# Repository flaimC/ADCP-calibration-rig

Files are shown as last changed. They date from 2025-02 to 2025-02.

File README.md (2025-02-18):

# ADCP-calibration-rig
This repo documents the design and build of an ADCP calibration rig for a Nortek Signature 100. The rig utilizes syntactic foam and a large footprint to stay afloat and stable in a calibration tank. It is designed to be lifted with an over-head crane while the ADCP is attached. Future versions of this calibration tool will include lasers, cameras, and motorized ball movement to expidite the calibration process.
adcpCalibrationRigAssy (3)

# Onshape CAD
This project was designed in a browser-based CAD program called Onshape. The document for this project can be found [here](https://cad.onshape.com/documents/10602cede9c07e59b6c9bb3e/w/70dcfadde18bdff9054825df/e/5ac3f072fa41a360b08c238f)

# ADCP calibration rig buoyancy calculation
### using Archimedes principle 
Archimedes principle states that the buoyancy of an object is equal to the mass of the water it displaces.

The buoyancy force of a fully submerged object is described as $F_B = V_{disp} \times \rho \times g$, where $V_{disp}$ is the displaced volume, $\rho$ is the density of the dsiplaced fluid, and $g$ is the gravitational constant.

We can expand on this equation to include the force of gravity acting upon the submerged object.

$$F_B = V_{disp} \times (\rho_{disp} - \rho_{object}) \times g$$

We can expand this equation and cancel out the gravitational constants to find the maximum mass a submerged volume of known density can support before being fully submerged.
$$M_{max} = V_{disp} \times (\rho_{disp} - \rho_{object})$$
For complex objects and geometries, the forces acting upon subcompenents need to be accounted.

$$M_{max} \times g = \left( \sum_{i=0}^n M_{i} \times g \right)$$
#### Define variables
Let,
$$B = \text{resultant maxium mass from chosen materials and volumes that can be supported without sinking},$$

$$\rho_{sw} = \text{assumed density of seawater in tech tank},$$
$$\rho_{syn} = \text{density of macrofoam-18 syntactic foam},$$
$$\rho_{hdpe} = \text{density of HDPE platstic sheet},$$
$$\rho_{misc} = \text{average density of submerged metal parts},$$

$$V_{syn} = \text{volume of syntactic foam},$$
$$V_{HDPE} = \text{volume of the HDPE sheet},$$
$$V_{misc} = \text{volume of submerged metal parts},$$

$$M_{ADCP} = \text{weight of ADCP in water},$$
$$M_{topmisc} = \text{weight of in-air metal parts}.$$
Note: The distrubtion of density variation does not matter for $\rho_{misc}$ since we are just looking for a buoyancy force, not stability. This density is calcuated from the total mass and volume of submerged metal parts (e.g., screws, nuts, rods).

#### Find the buoyancy
A buoyancy force is only calculated for submerged objects. The full mass of in-air objects is subtracted from the total bouancy. The top of the ADCP is not submerged, but the weight is nearly wholely contained at the bottom of the ADCP, so we are assuming the in-air weight of the top two-inches of the ADCP is negligible. Surface tension is also assumed to be negligible in this calculation.

$$B = V_{syn}(\rho_{sw}-\rho_{syn}) + V_{hdpe}(\rho_{sw}-\rho_{hdpe}) + V_{misc}(\rho_{sw}-\rho_{misc}) - M_{adcp} - M_{topmisc}$$

If $B > 0$, then the ADCP calibration rig should float. If $B < 0$, then the ADCP calibration rig should sink.

Given,

$$\rho_{sw} = 1035\text{ kg•m}^{-3},$$
$$\rho_{syn} = 290\text{ kg•m}^{-3},$$
$$\rho_{hdpe} = 941\text{ kg•m}^{-3},$$
$$\rho_{misc} = 3910.26\text{ kg•m}^{-3},$$

$$V_{syn} = 0.05968\text{ m}^3,$$
$$V_{HDPE} = 0.00509\text{ m}^3,$$
$$V_{misc} = 0.001306\text{ m}^3,$$

$$M_{ADCP} = 13\text{ kg},$$
$$M_{topmisc} = 4.8144\text{ kg}.$$

We can plug these values into our buoyancy equation and find the maximum in-air weight the calibration rig can hold before being completely submerged.

$$B = 0.05968 \text{ m}^3(1035 \text{ kg•m}^{-3}-290\text{ kg•m}^{-3}) +$$ 
$$0.00509\text{ m}^3(1035\text{ kg•m}^{-3}-941\text{ kg•m}^{-3}) +$$ 
$$0.001306\text{ m}^3(1035\text{ kg•m}^{-3}-3910.26\text{ kg•m}^{-3}) - 13\text{ kg}- 4.8144\text{ kg}$$

$$B=23.37 \text{ kg}$$

# Disclaimer
This repository is a scientific product and is not official communication of the National Oceanic and Atmospheric Administration, or the United States Department of Commerce. All NOAA GitHub project code is provided on an ‘as is’ basis and the user assumes responsibility for its use. Any claims against the Department of Commerce or Department of Commerce bureaus stemming from the use of this GitHub project will be governed by all applicable Federal law. Any reference to specific commercial products, processes, or services by service mark, trademark, manufacturer, or otherwise, does not constitute or imply their endorsement, recommendation or favoring by the Department of Commerce. The Department of Commerce seal and logo, or the seal and logo of a DOC bureau, shall not be used in any manner to imply endorsement of any commercial product or activity by DOC or the United States Government.

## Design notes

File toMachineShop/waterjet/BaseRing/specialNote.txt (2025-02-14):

Note: It is intended for the counter bore hole to be done after the main hole is water jet cut.

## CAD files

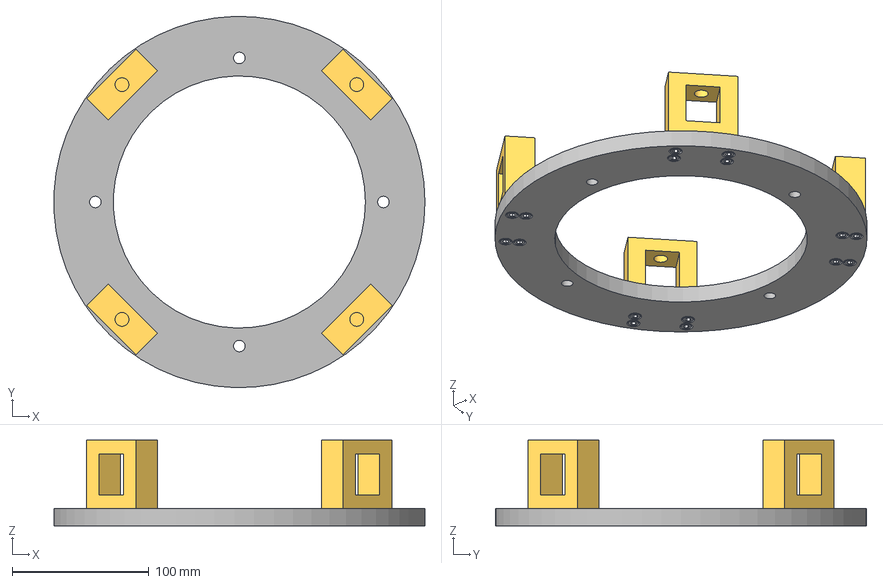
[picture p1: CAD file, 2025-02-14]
stlFiles/mountAssy.step
270.8 x 270.9 x 62.7 mm
AdcpMountBlock x 4
AdcpMountBasePlate
10-32 1in x 16

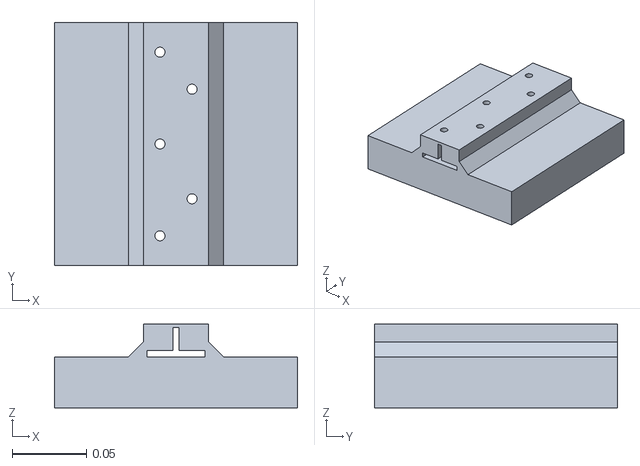
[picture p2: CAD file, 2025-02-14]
stlFiles/3dPrintable/ballast - outriggerMount.stl
0.164 x 0.164 x 0.0566

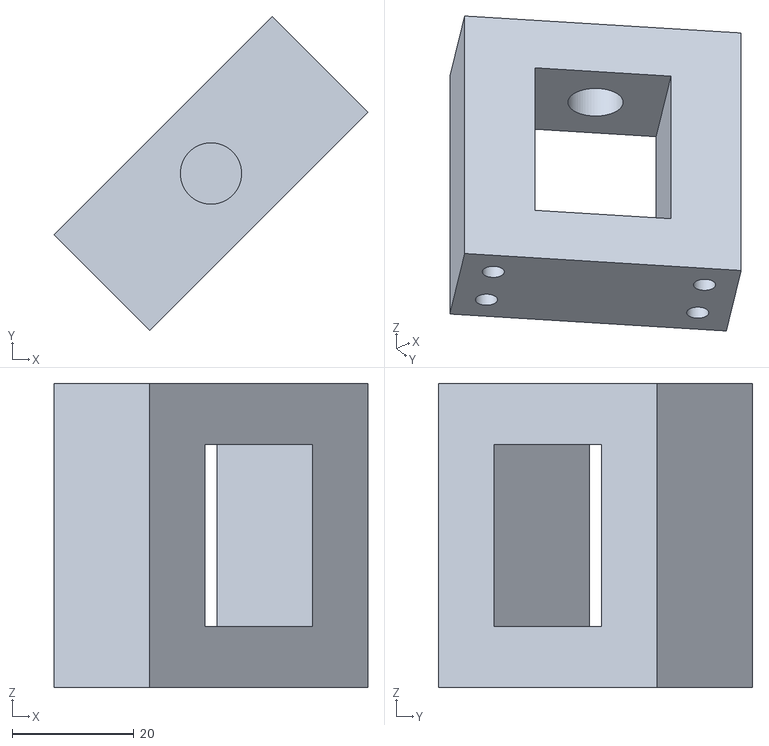
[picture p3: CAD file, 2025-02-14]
toMachineShop/machined/mountBlock/mountBlock.stl
51.6 x 51.6 x 50.0

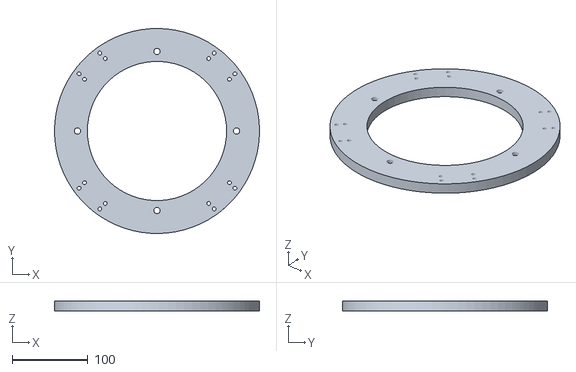
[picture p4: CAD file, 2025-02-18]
toMachineShop/waterjet/adcpMountBasePlate/AdcpMountBasePlate.stl
271.0 x 270.9 x 12.7

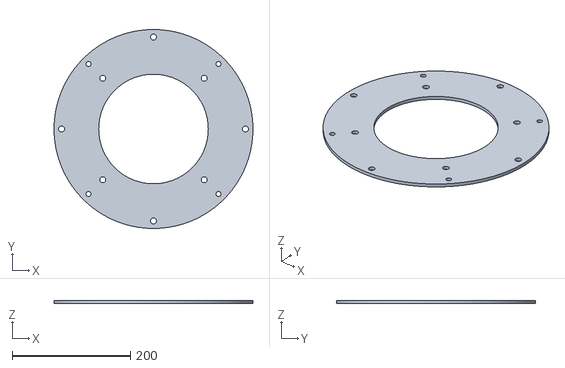
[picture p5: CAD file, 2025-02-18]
toMachineShop/waterjet/BaseRing/baseRing.stl
336.0 x 336.0 x 5.00

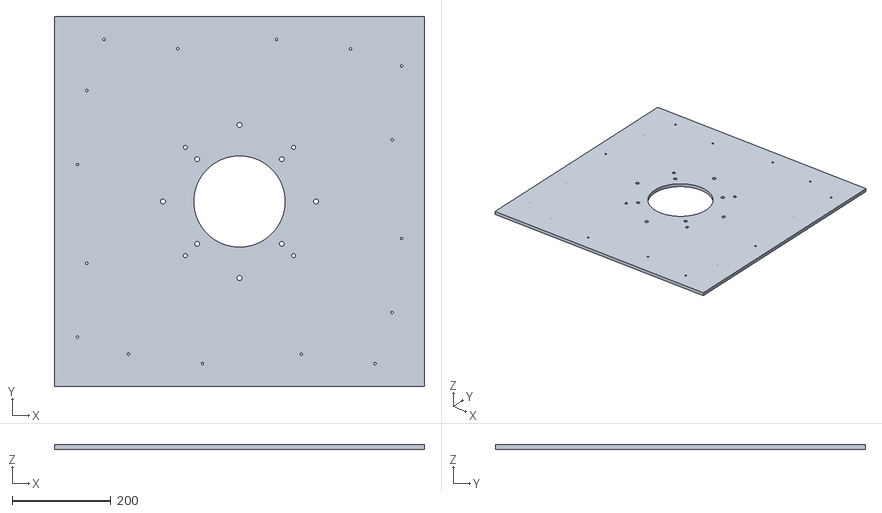
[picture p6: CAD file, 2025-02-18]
toMachineShop/waterjet/hdpeBase/hdpeBase.stl
750.0 x 750.0 x 9.52

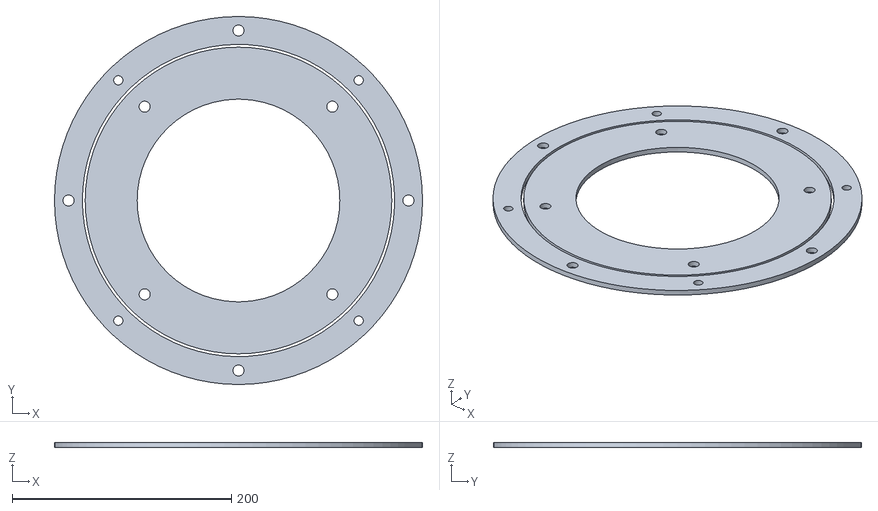
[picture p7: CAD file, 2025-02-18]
toMachineShop/waterjet/topRingAdcpRing/topRingAdcpRing.stl
336.0 x 336.0 x 4.83

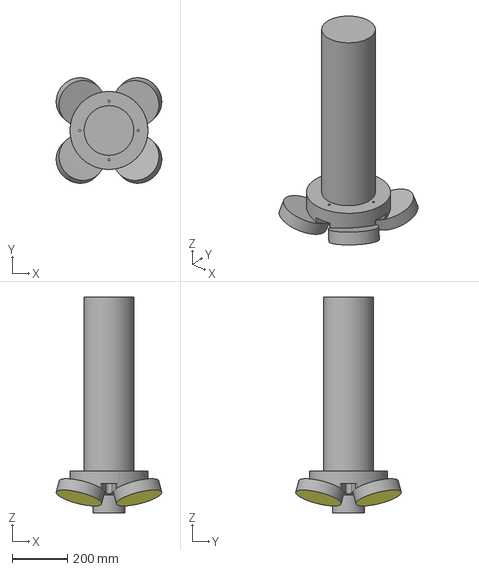
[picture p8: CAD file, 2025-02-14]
stlFiles/adcpCalibrationRig - ADCP.step
380.7 x 380.7 x 778.5 mm

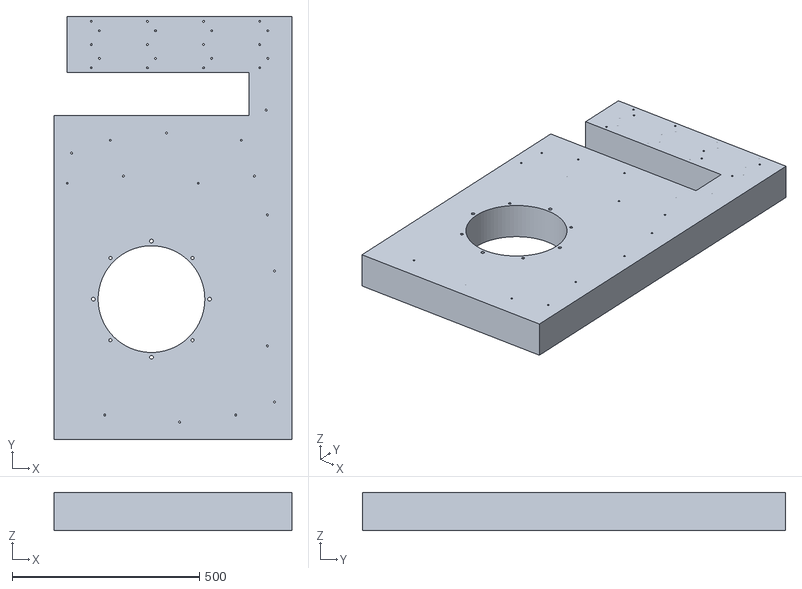
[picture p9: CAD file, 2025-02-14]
toMachineShop/waterjet/ballast/ballast.stl
635.0 x 1130.0 x 101.6

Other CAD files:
toMachineShop/modelsForReference/mountAssy.step
dwgFiles/hdpeCut.dwg
toMachineShop/waterjet/ballast/ballastCut.dwg
toMachineShop/waterjet/ballast/separateBallastFiles/ballast6.dwg
dwgFiles/halfInchAluminumCut.dwg
toMachineShop/waterjet/adcpMountBasePlate/adcpMountBasePlateCut.dwg
toMachineShop/waterjet/ballast/separateBallastFiles/ballast4.dwg
toMachineShop/waterjet/BaseRing/baseRingCut.dwg
toMachineShop/waterjet/hdpeBase/hdpeCut.dwg
dwgFiles/baseRingCut.dwg
dwgFiles/syntacticFoamCut.dwg
toMachineShop/waterjet/ballast/separateBallastFiles/ballast1.dwg
toMachineShop/waterjet/ballast/separateBallastFiles/ballast2.dwg
toMachineShop/waterjet/ballast/separateBallastFiles/ballast3.dwg
toMachineShop/waterjet/ballast/separateBallastFiles/ballast5.dwg
toMachineShop/waterjet/ballast/separateBallastFiles/ballast7.dwg
toMachineShop/waterjet/topRingAdcpRing/topRingAdcpRingCut.dwg

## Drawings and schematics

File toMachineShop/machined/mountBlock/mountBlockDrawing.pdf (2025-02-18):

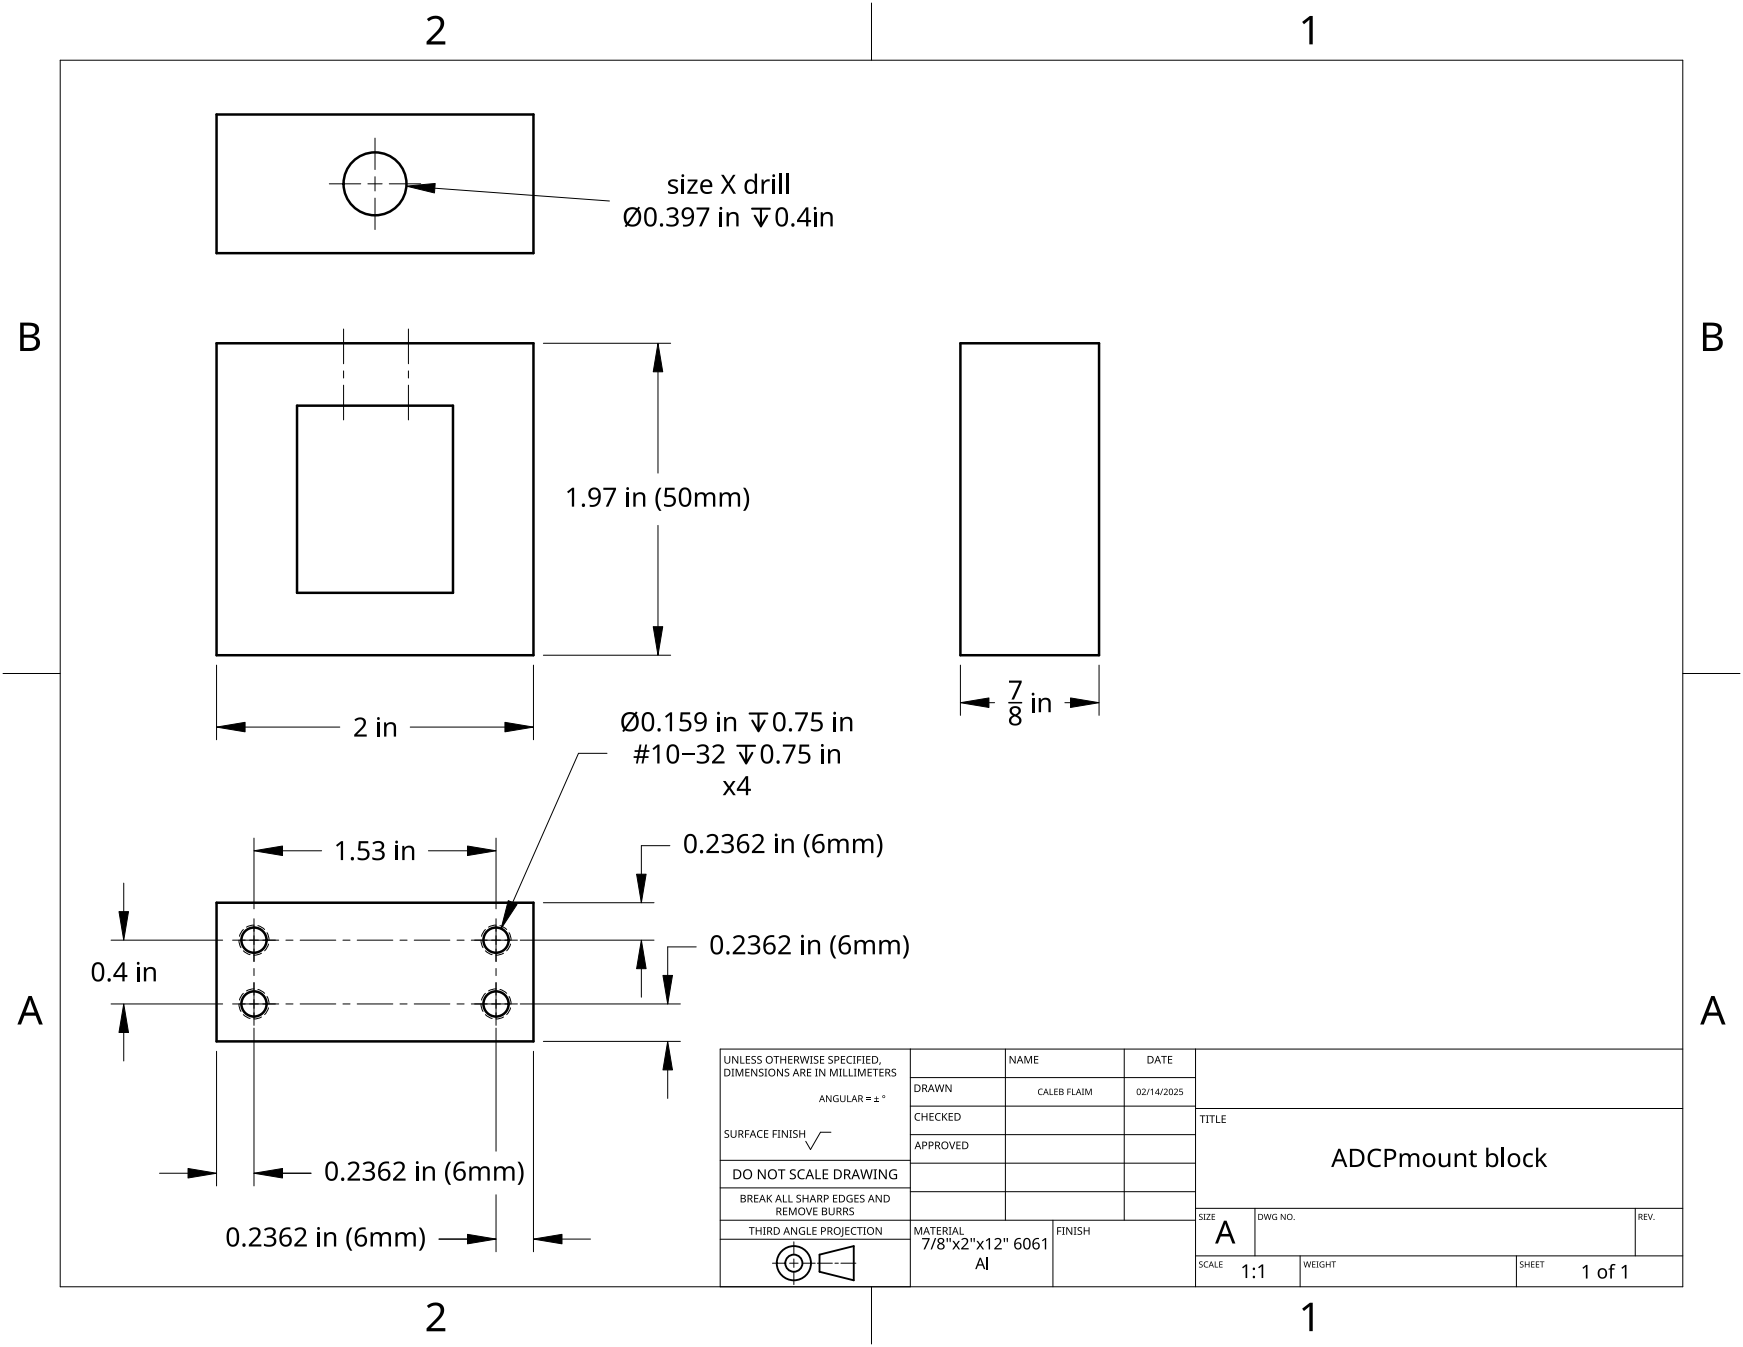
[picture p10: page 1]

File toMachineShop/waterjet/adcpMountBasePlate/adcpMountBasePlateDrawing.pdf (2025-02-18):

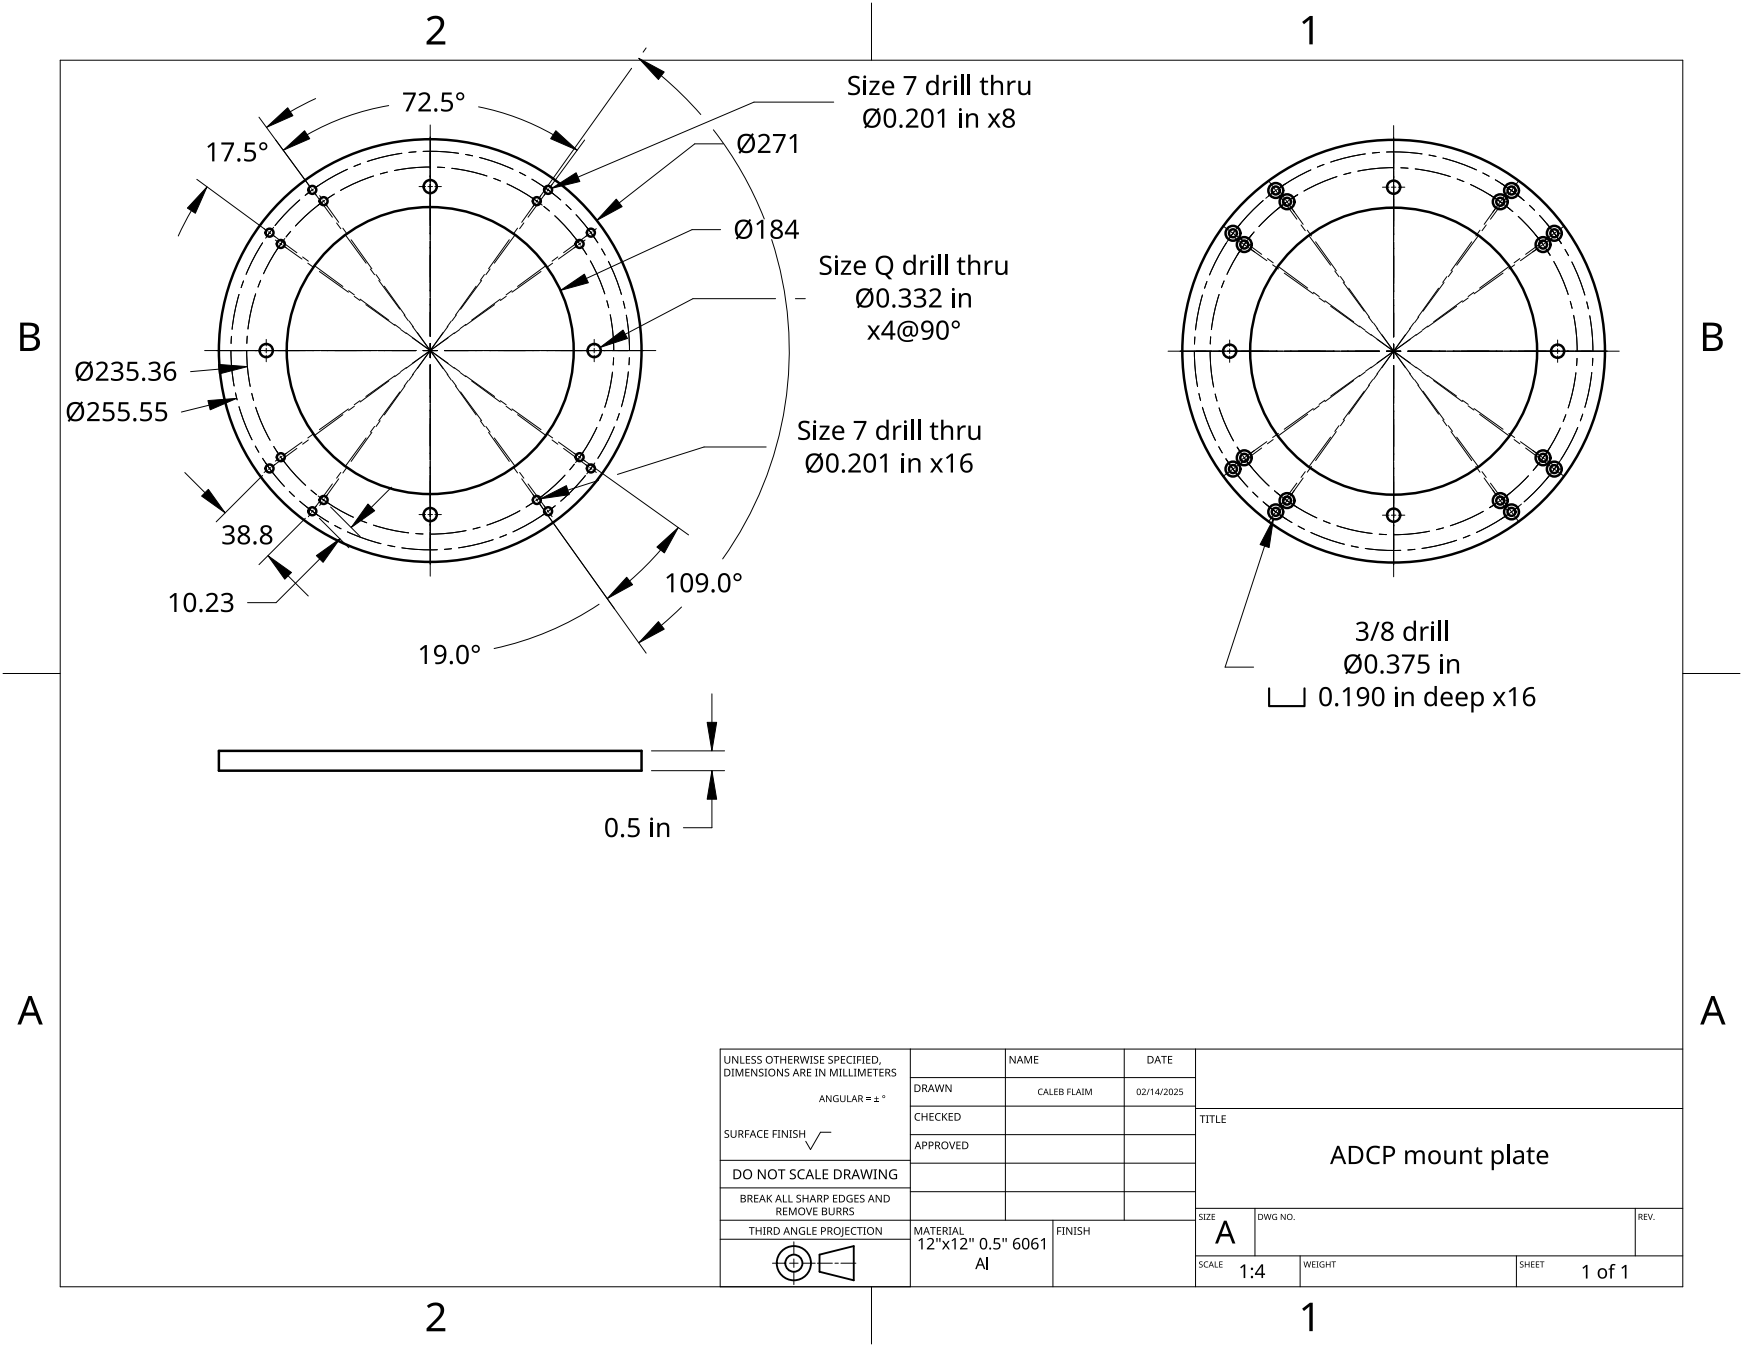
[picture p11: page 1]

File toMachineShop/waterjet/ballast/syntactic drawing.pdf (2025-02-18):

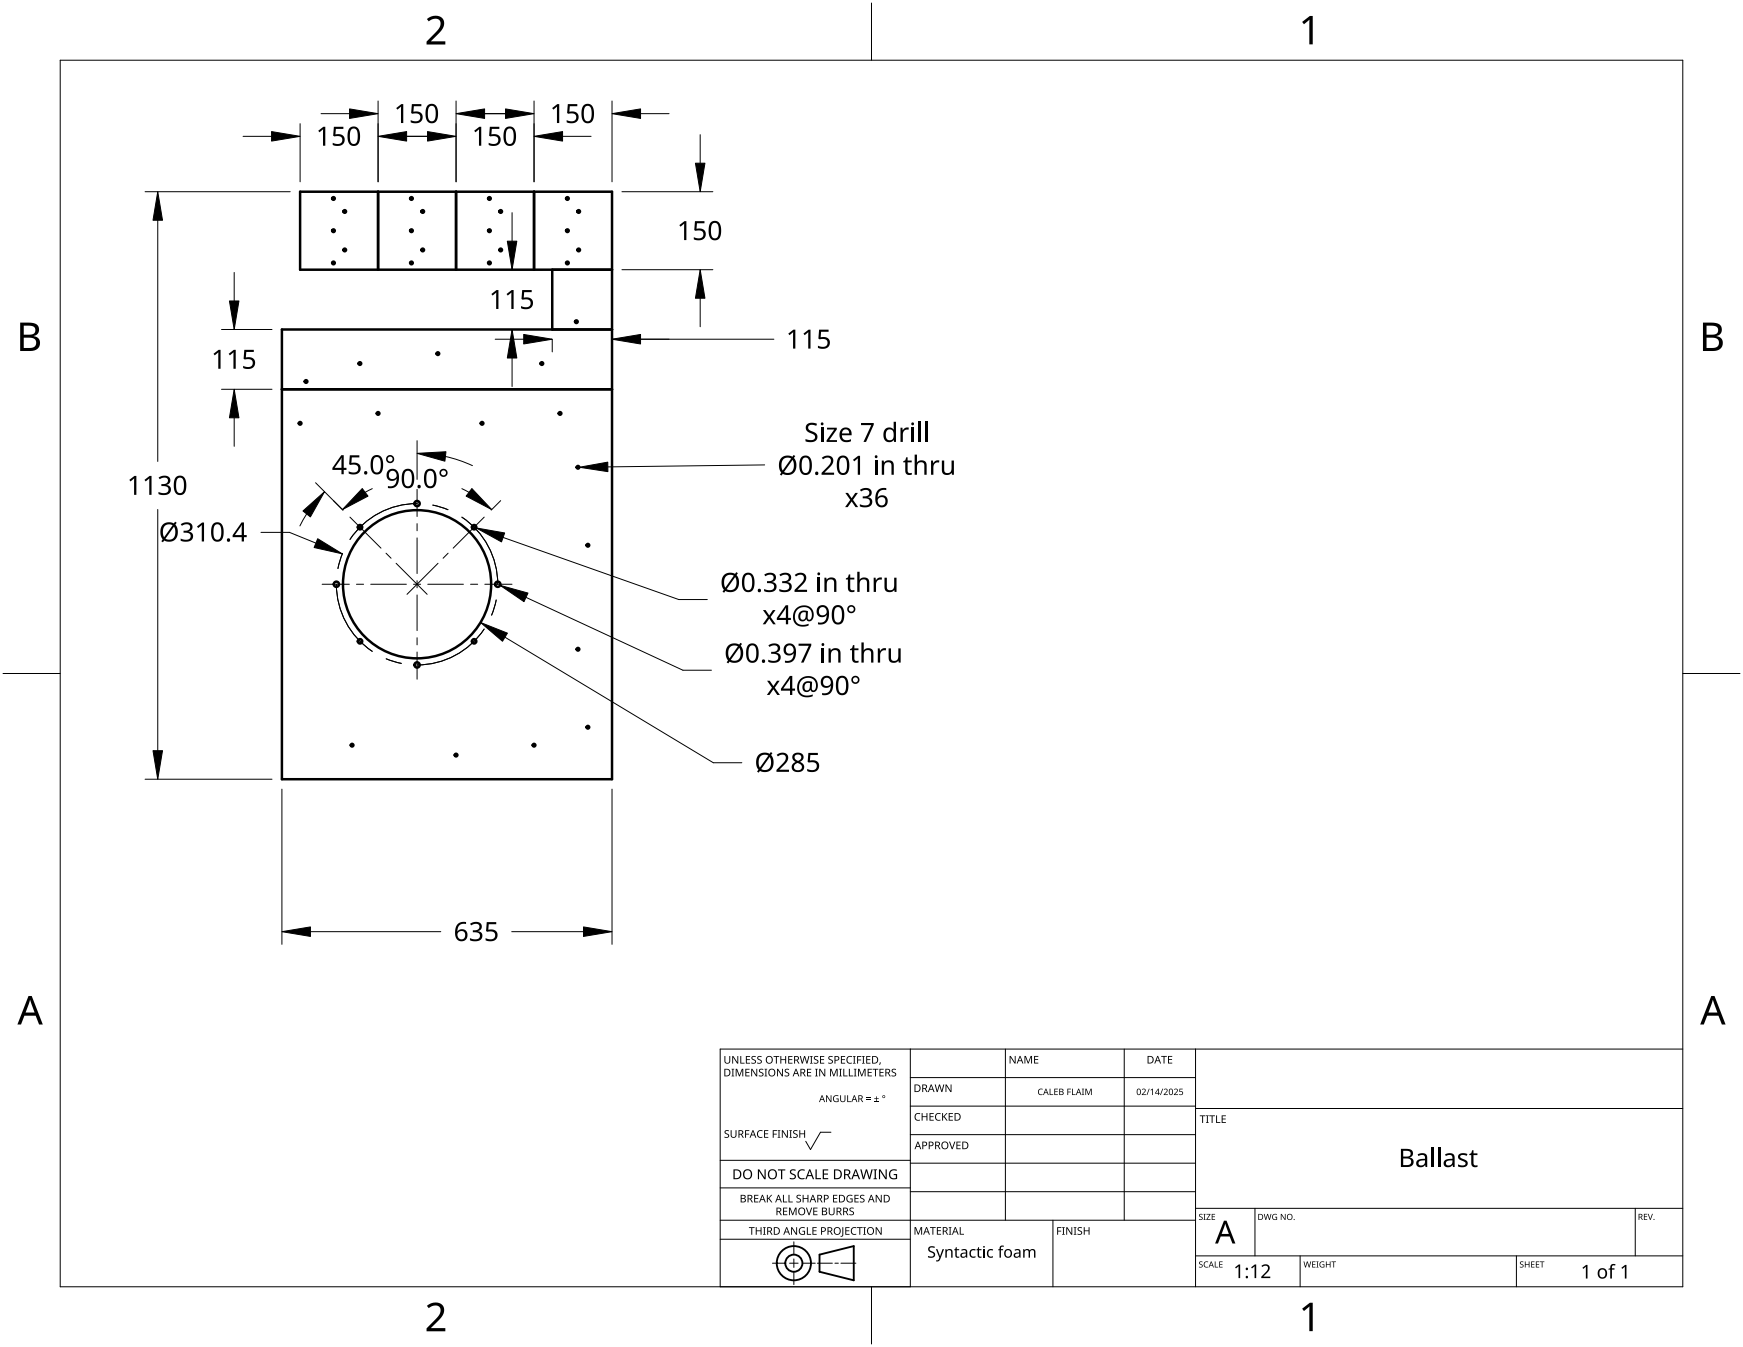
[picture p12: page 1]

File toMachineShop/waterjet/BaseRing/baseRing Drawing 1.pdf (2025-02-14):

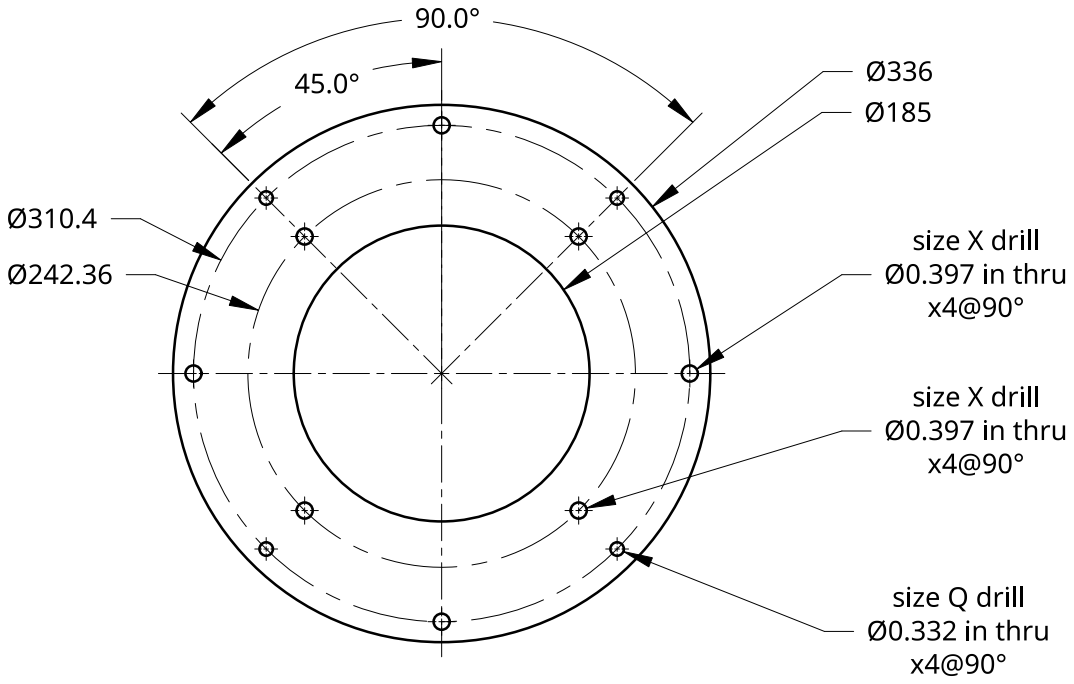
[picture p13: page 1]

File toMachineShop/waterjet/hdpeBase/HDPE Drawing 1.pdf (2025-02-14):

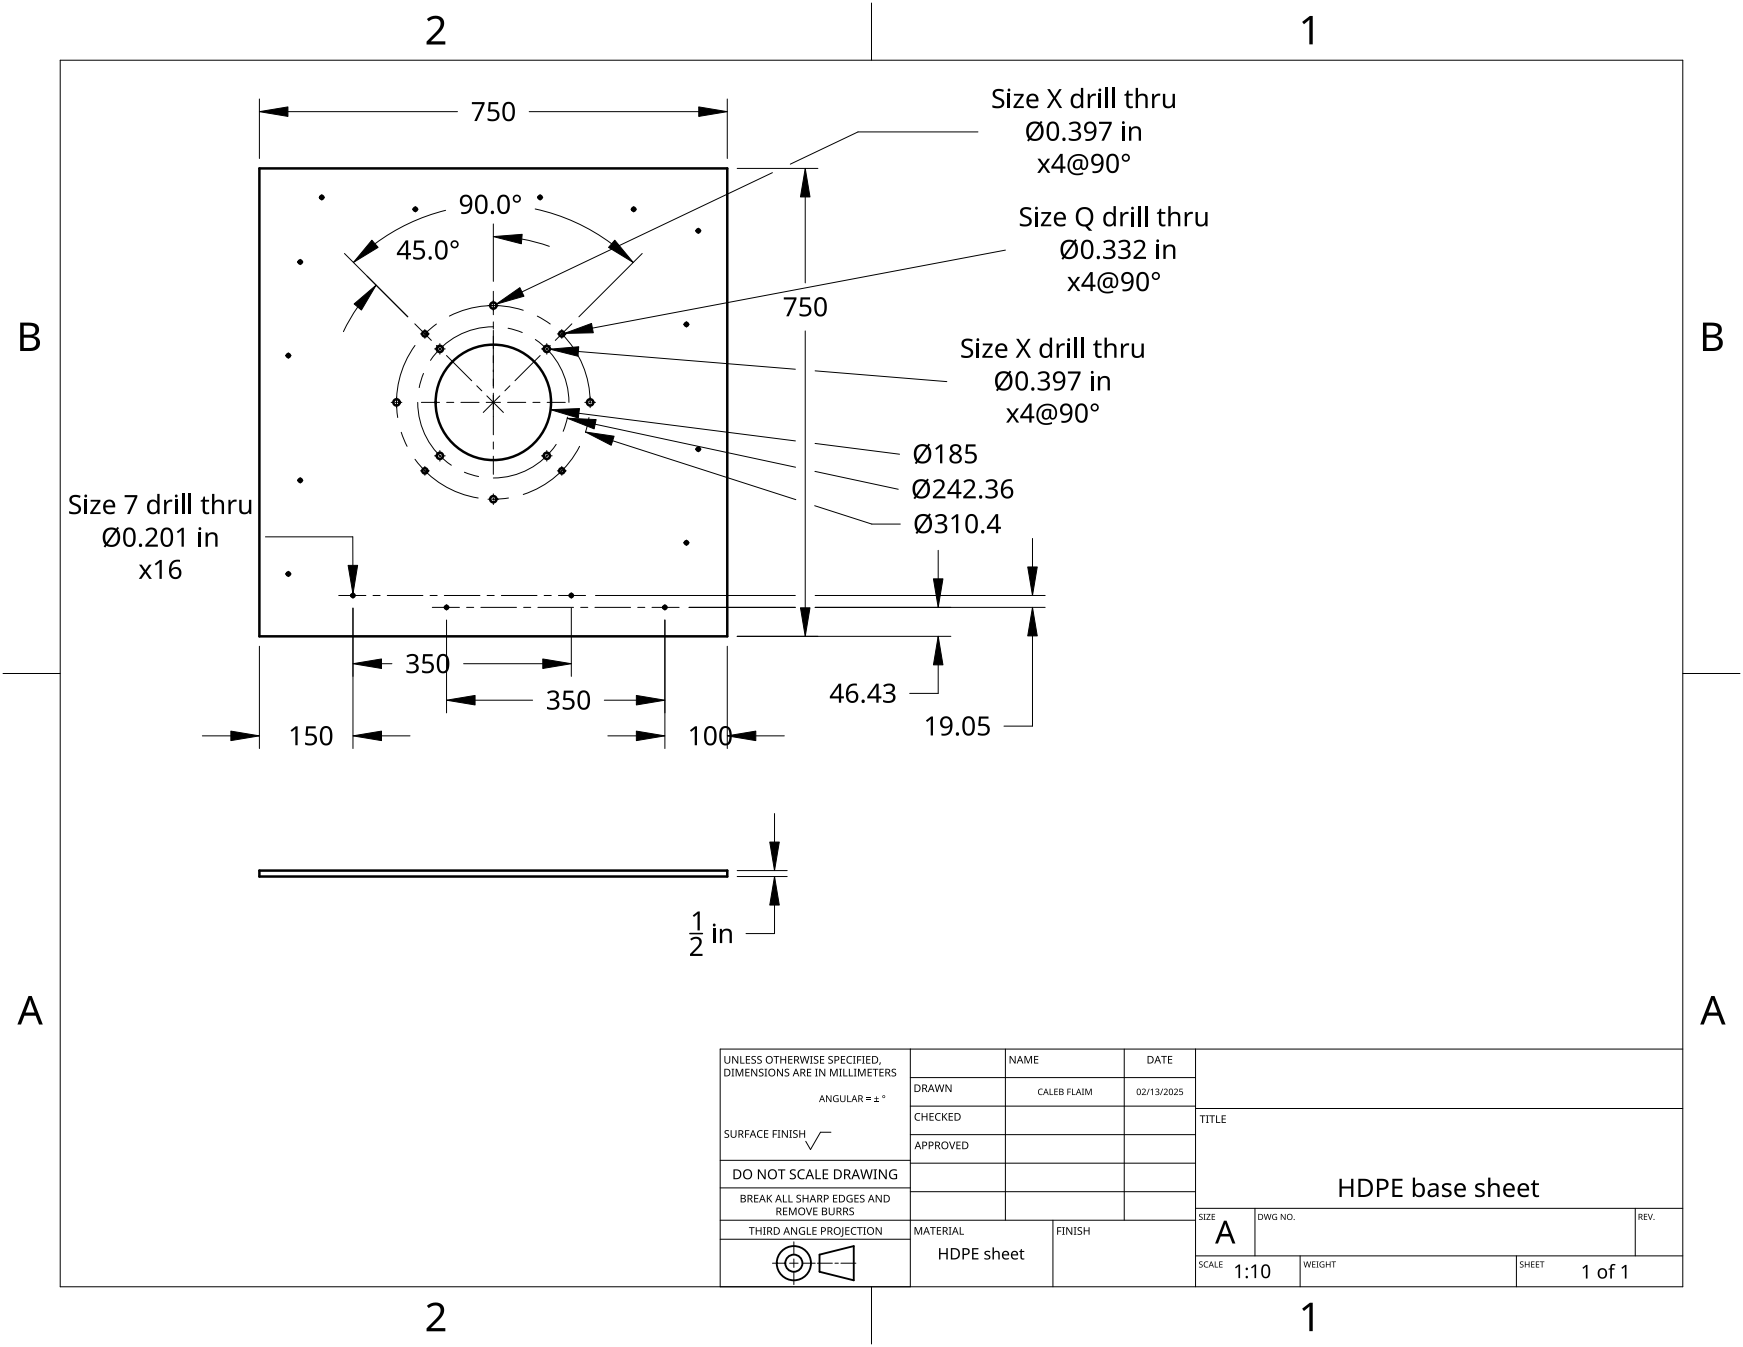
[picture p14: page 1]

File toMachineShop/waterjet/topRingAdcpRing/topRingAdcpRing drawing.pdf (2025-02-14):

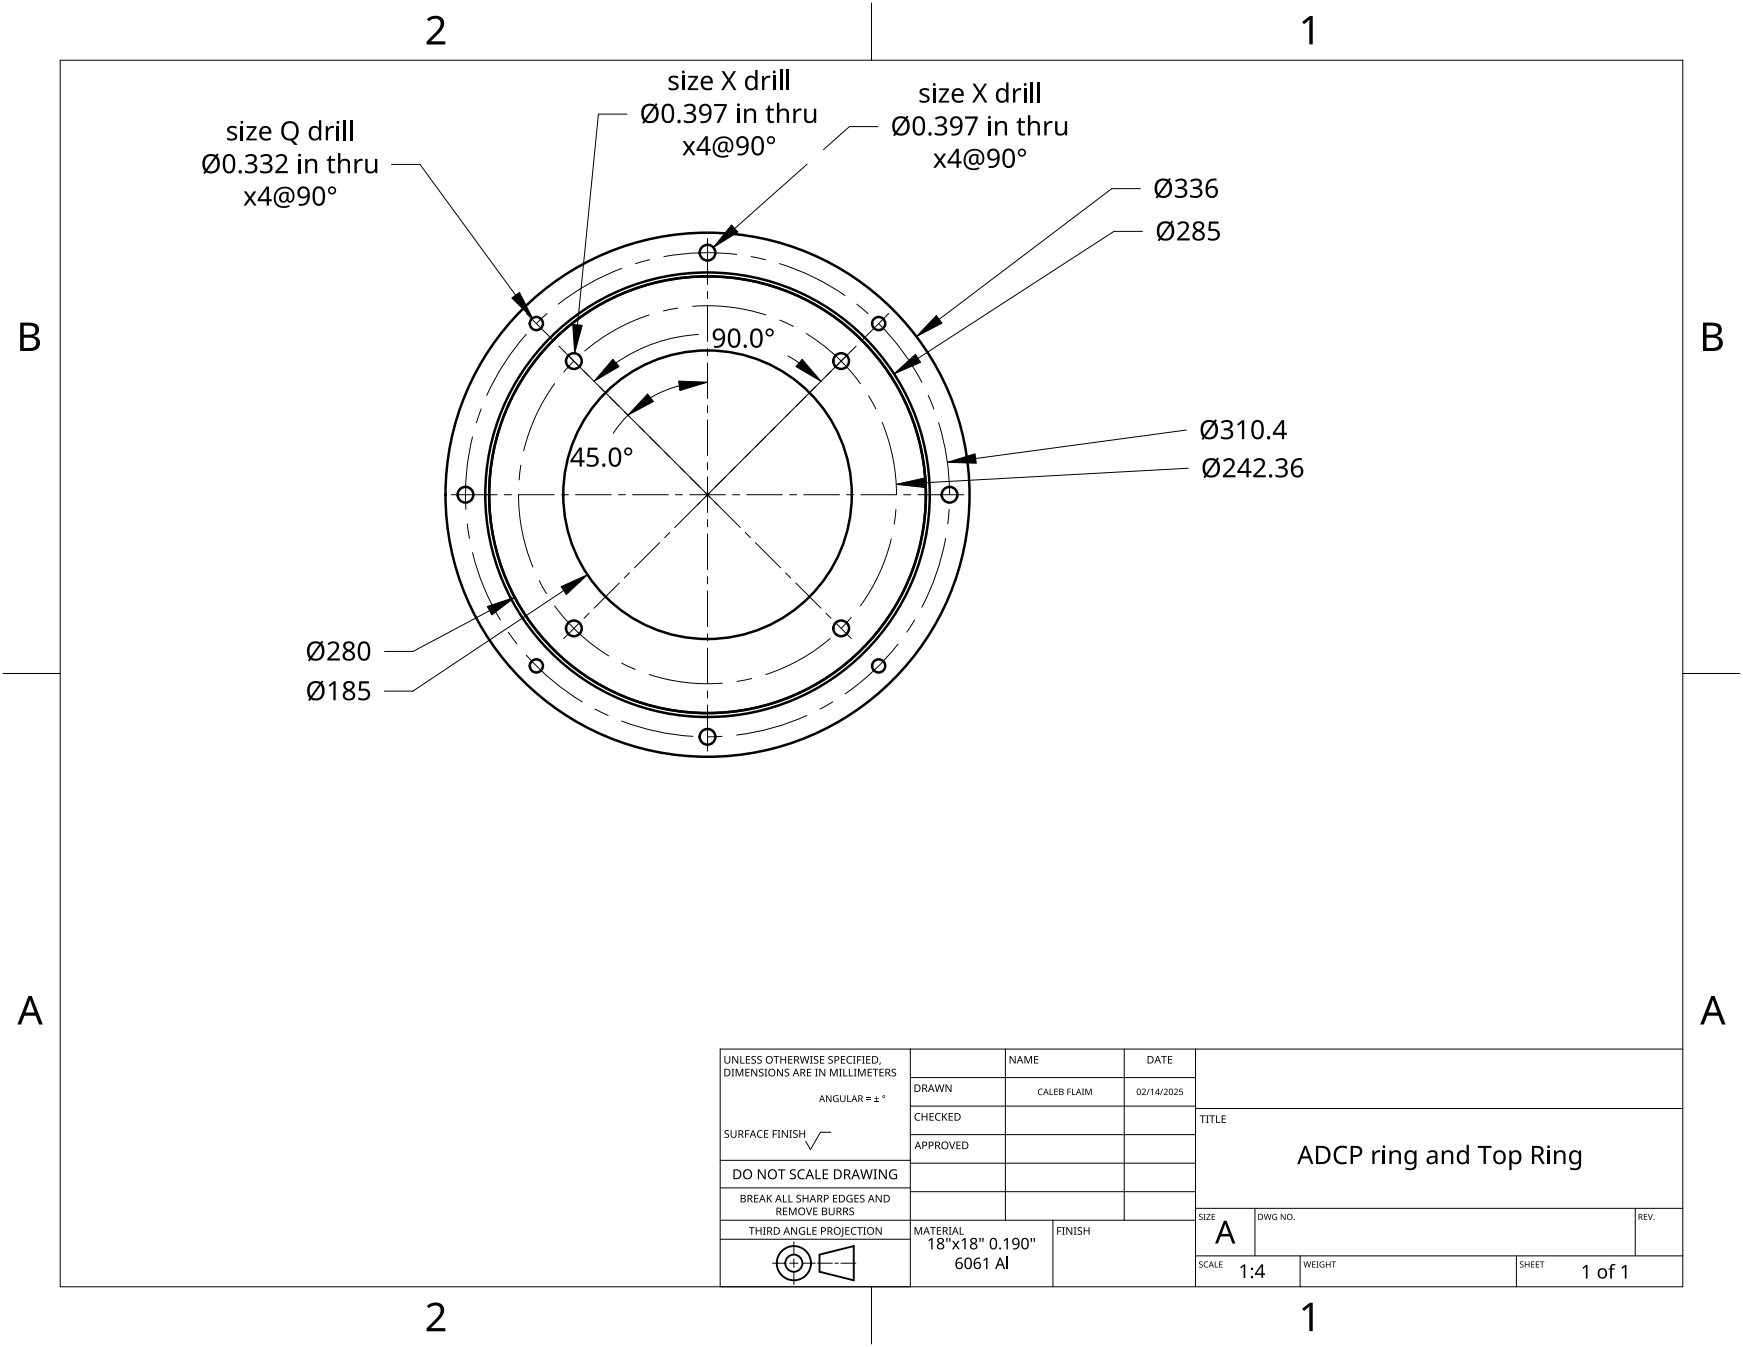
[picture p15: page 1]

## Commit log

2025-02-14 added files for machining
    added files for machining. The "toMachineShop" folder can be sent to the machine shop along with materials.
    [adcpCalibrationRig - AdcpMountBlock (1).stl, adcpMountBasePlateCut.dwg, ballast - outriggerMount.stl, ballast.stl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]
2025-02-14 added step files of parts
    [adcpCalibrationRig - ADCP.step, ballast - outriggerMount.stl, mountAssy.step]
2025-02-18 adjusted drawings and added stls
    [AdcpMountBasePlate.stl, ballast.stl, ballastCut.dwg, baseRing.stl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]
2025-02-19 added separate DWG
    waterjet parts can't have shared borders for the DWGs due to kerf, so I separated each part into its own file.
    [ballast1.dwg, ballast2.dwg, ballast3.dwg, ballast4.dwg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]
